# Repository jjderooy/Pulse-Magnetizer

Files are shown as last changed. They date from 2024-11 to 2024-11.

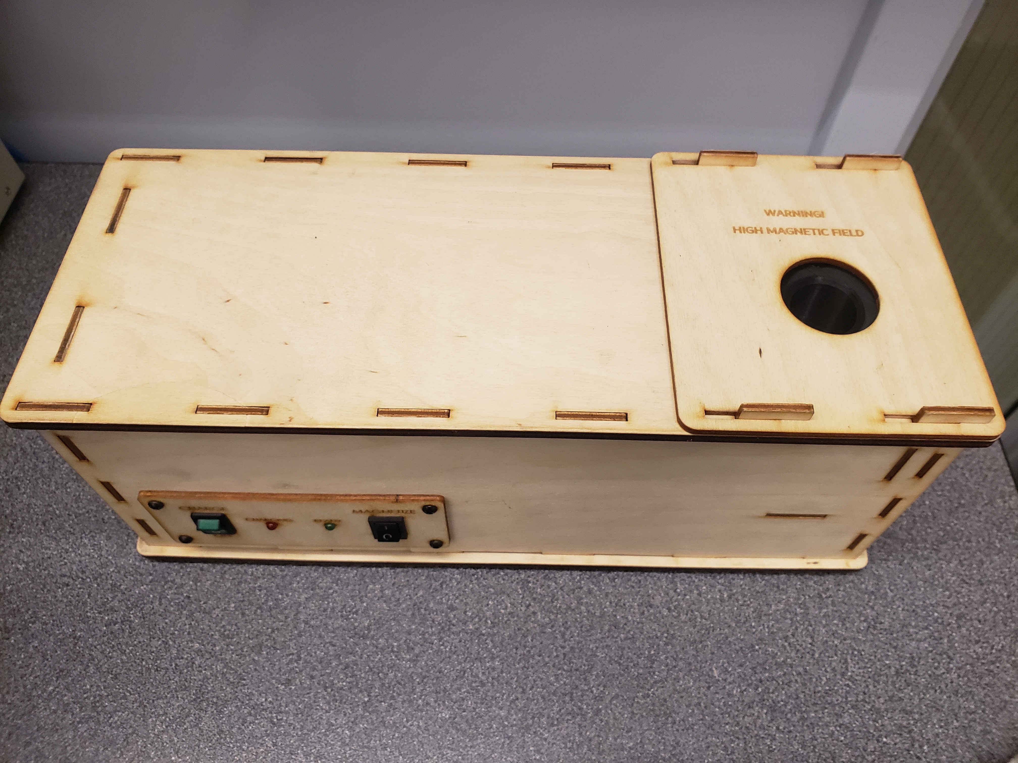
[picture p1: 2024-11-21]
Media/assembled.jpg

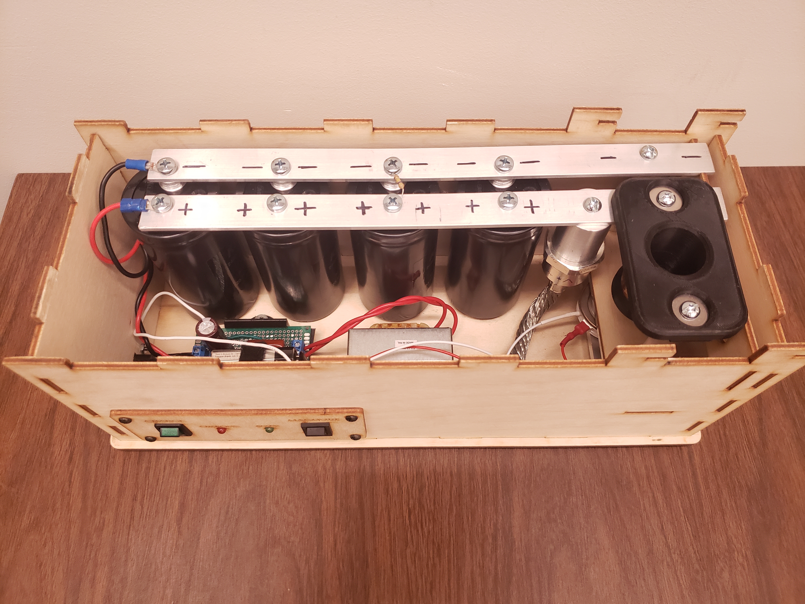
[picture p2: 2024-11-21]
Media/open_top.jpg

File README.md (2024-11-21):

# Pulse-Magnetizer
For research involving magnets, it is often required to magnetize unmagnetized permanent magnets by exposing them to a strong field. For neodymium (NdFeB) magnets, this can pose quite a challenge because the fields required to permanently magnetize them are very strong. Commercial magnetizers exist but are large and expensive and not well suited for occasional lab use.

Fortunately, Yuri Skvortsov published his design of a [pulse magnetizer](https://medium.com/@yuriy.skvortsov/pulse-re-magnetizer-for-neodymium-magnets-e5c42aefbf78) using a capacitor bank and coil to remagnetize hard drive magnets which was an excellent starting point for this project. This repository contains a modifed version of Yuri's that aims to improve safety and functionality with a basic control panel, laser cut wooden case, and basic build instructions.

## Contents
- Complete KiCAD schematic for use with 120VAC mains
- CSV bill of materials for all electrical components
- SVG for laser cut 3mm and 6mm plywood to construct housing
- STEP file CAD assembly

## Performance
A simple test to verify the functionality of the pulse magnetizer was conducted by measuring and recording the pull force of a 0.75" diameter, 0.1875" thick NdFeB disc magnet acting on a steel disk placed on a gram scale. The magnet was then heated using a heat gun to above its curie point to remove any magnetic properties. After cooling, the magnet was exposed to a full pulse from the magnetizer and measured using the gram scale again. The scale indicated the field was 98.5% of the original strength. This is not a perfect test because the grade of the magnet was not known (likely a lower grade e.g. N40), and could struggle to remagnetize higher grades like N55. Based on SPICE simulations and theoretical calculations for a 30mm diameter, 30mm long, 30 turn coil using 1mm diameter copper wire, the field strength generated was 3.5T. This could be further improved using the same dimension coil but with 1.5mm diameter wire (by reducing inductance and resistance allowing more current flow), to generate a 4.3T field. This is plenty strong for even N55 magnets.

## Safety
This device deals with lethally high voltages, and capacitors that can maintain these voltages even after the device is unplugged. Any use of this project is at your own risk.

## Build
In addition to the electronics BOM, some basic wiring hardware is needed (wire, spade connectors, soldering iron, screw terminals, proto-board). Screws are not included on the BOM, but are M5 for the capacitors, and #10 machine screws elsewhere. A small quantity of plywood (both 3mm and 6mm thickness) is needed for the lasercut enclosure. All lasercut parts are compensated for a 0.008" kerf. The user will need to create shop drawings for the machined components because this is specific to the machining capabilites at hand.

Reference the .STEP file using a CAD program (e.g. FreeCAD) for assembly of all mechanical components. Two proto-boards are needed, one for the high voltage power supply, and one for the control panel. Images are included for a rough layout, but overall are left to the user to implement.

The spool for the coil is designed for 3D printing to allow customization of the coil dimensions. Care must be taken when manufacturing coils due to the high forces exerted on conductors during magnetizing. The coil had a tendancy to squish axially causing turns of the coil to overlap reducing uniformity of the field. To prevent this, it is recommended to wind the coil tightly and coat lightly with adhesive such as cyanoacrylate before wrapping with a few layers of polyimide (kapton) tape.

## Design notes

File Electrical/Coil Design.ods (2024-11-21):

Use this sheet to optimize coils. More turns increases the field strength, but also increases resistance and inductance which limit current and reduce field strength. Use the computed resistance and inductance values in a KiCAD or LTspice simulator with a 9600uF 340V capacitor bank to determine current. Use this peak current to calculate the B field. Nd magnets require at least 2T to be magnetized, but note that this calculator assumes an ideal solenoid which really only applies to long coils of wire so give some headroom.
Input | Intermediate | Output
Solenoid
 |  |  | 30L 30ID 1mm wire
Parameter | Value | Units | Field: 3.5T
Length | 30.00 | mm
Inner Dia. | 30.00 | mm
Outer Dia. | 32.00 | mm
Copper Dia. | 1.00 | mm
Conductivity | 5.80E+07 | S/m
Rel. Perm | 1.00 | -
Vac. Perm | 1.26E-06 | -
Wire Dia. | 1.01 | mm | 30L 30ID 1.5mm wire
Turns/Length | 30.00 | - | Field: 4.3T
Layers | 0.99 | -
Total Turns | 30.00 | -
Total Length | 2.86 | m
Resistance | 0.063 | Ohm
Inductance | 28.45 | uH
Current | 3,000.00 | A
B | 3.770 | T

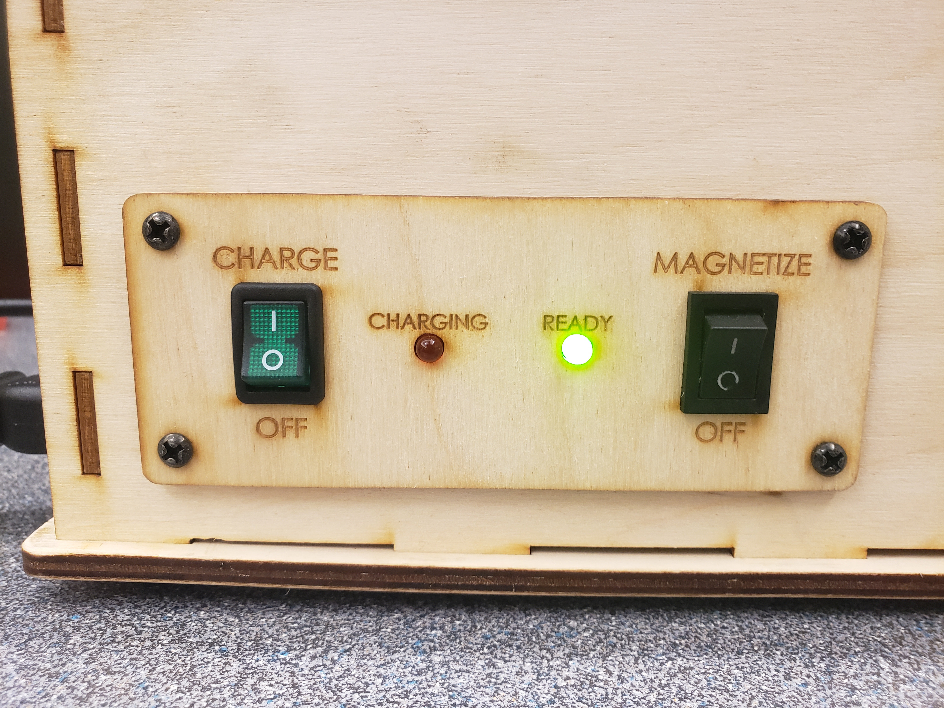
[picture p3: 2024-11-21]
Media/control_panel.jpg

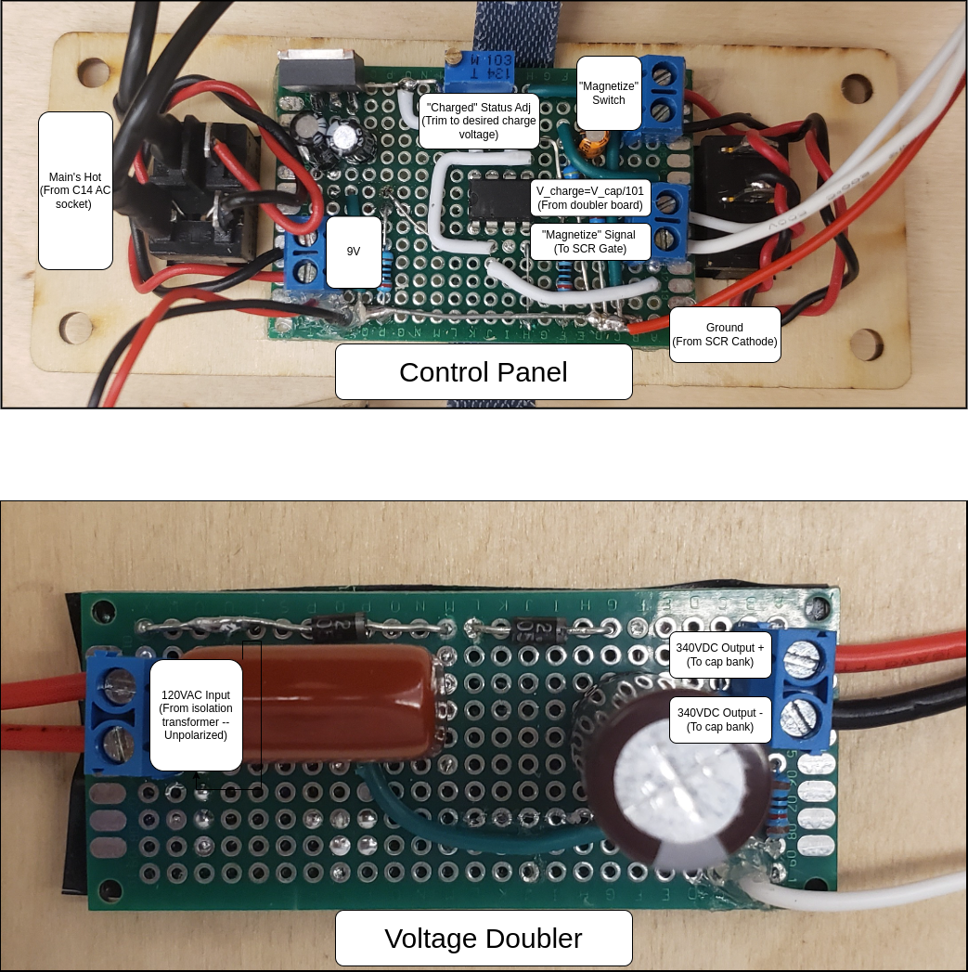
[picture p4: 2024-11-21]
Media/proto_boards.png

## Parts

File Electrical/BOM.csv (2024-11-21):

Index | Manufacturer Part Number | Manufacturer Name | Description | Requested Quantity 1 | Pack Quantity 1 | Pack Type 1 | Digi-Key Part Number 1 | Unit Price 1 | Extended Price 1 | Minimum Order Quantity 1
1 | N-48X | Triad Magnetics | XFRMR ISOL 115V TO 115V 15VA | 1 | 1 | Box | 237-1856-ND | 22.25 | $22.25 | 1
2 | ALS80A242KF400 | KEMET | CAP ALUM 2400UF 20% 400V SCREW | 4 | 4 | Bulk | ALS80A242KF400-ND | 55.41 | $221.64 | 1
3 | 1N4005-TP | Micro Commercial Co | DIODE GEN PURP 600V 1A DO41 | 10 | 10 | Cut Tape (CT) | 1N4005-TPMSCT-ND | 0.173 | $1.73 | 1
4 | VS-400U160D | Vishay General Semiconductor - Diodes Division | DIODE GP 1.6KV 400A DO205AB | 1 | 1 | Bulk | VS-400U160DGI-ND | 85.24 | $85.24 | 1
5 | VS-ST330C12C0 | Vishay General Semiconductor - Diodes Division | SCR 1.2KV 1420A TO200AB | 1 | 1 | Bulk | ST330C12C0-ND | 138.1 | $138.10 | 1
6 | CF12JT470K | Stackpole Electronics Inc | RES 470K OHM 5% 1/2W AXIAL | 1 | 1 | Cut Tape (CT) | CF12JT470KCT-ND | 0.16 | $0.16 | 1
7 | ECW-FD2W225J | Panasonic Electronic Components | CAP FILM 2.2UF 5% 450VDC RADIAL | 2 | 2 | Bulk | PCF1609-ND | 1.09 | $2.18 | 1
8 | 703W-00/04 | Qualtek | PWR ENT RCPT IEC320-C14 PANEL QC | 1 | 1 | Bulk | Q212-ND | 1.56 | $1.56 | 1
9 | RA1113112R | E-Switch | SWITCH ROCKER SPST 10A 125V | 1 | 1 | Bulk | EG5619-ND | 1 | $1.00 | 1
10 | LRA32H2FBBNN | ZF Electronics | SWITCH ROCKER DPST 10A 125V | 1 | 1 | Bulk | CH770-ND | 2.67 | $2.67 | 1
11 | 232 | Keystone Electronics | BATT CONNECTOR SNAP 9V 4" LEADS | 1 | 1 | Bulk | 36-232-ND | 0.9 | $0.90 | 1
12 | CF14JT200R | Stackpole Electronics Inc | RES 200 OHM 5% 1/4W AXIAL | 10 | 10 | Cut Tape (CT) | CF14JT200RCT-ND | 0.055 | $0.55 | 1
13 | CF14JT1M00 | Stackpole Electronics Inc | RES 1M OHM 5% 1/4W AXIAL | 10 | 10 | Cut Tape (CT) | CF14JT1M00CT-ND | 0.055 | $0.55 | 1
14 | CF14JT10K0 | Stackpole Electronics Inc | RES 10K OHM 5% 1/4W AXIAL | 10 | 10 | Cut Tape (CT) | CF14JT10K0CT-ND | 0.055 | $0.55 | 1
15 | CF14JT4K70 | Stackpole Electronics Inc | RES 4.7K OHM 5% 1/4W AXIAL | 10 | 10 | Cut Tape (CT) | CF14JT4K70CT-ND | 0.055 | $0.55 | 1
16 | ECA-1JM100LW | Panasonic Electronic Components | CAP ALUM 10UF 20% 63V RADIAL TH | 1 | 1 | Cut Tape (CT) | P19535CT-ND | 0.22 | $0.22 | 1
17 | LM358P | Texas Instruments | IC OPAMP GP 2 CIRCUIT 8DIP | 1 | 1 | Tube | 296-1395-5-ND | 0.36 | $0.36 | 1
18 | LM7805CT/NOPB | Texas Instruments | IC REG LINEAR 5V 1A TO220-3 | 1 | 1 | Tube | 296-47192-ND | 2.72 | $2.72 | 1
19 | N6L30T0N-103-3030 | Amphenol Piher Sensing Systems | TRIMMER 10K OHM 0.1W PC PIN TOP | 1 | 1 | Bulk | 1993-N6L30T0N-103-3030-ND | 0.72 | $0.72 | 1
20 | C320C104K5R5TA | KEMET | CAP CER 0.1UF 50V X7R RADIAL | 2 | 2 | Bulk | 399-4264-ND | 0.35 | $0.70 | 1
21 | MT4118-HR-A | Marktech Optoelectronics | LED RED DIFFUSED 5MM ROUND T/H | 1 | 1 | Bulk | 1125-1188-ND | 0.47 | $0.47 | 1
22 | MT2118-G-A | Marktech Optoelectronics | LED GREEN DIFFUSED 5MM ROUND T/H | 1 | 1 | Bulk | 1125-1184-ND | 0.45 | $0.45 | 1

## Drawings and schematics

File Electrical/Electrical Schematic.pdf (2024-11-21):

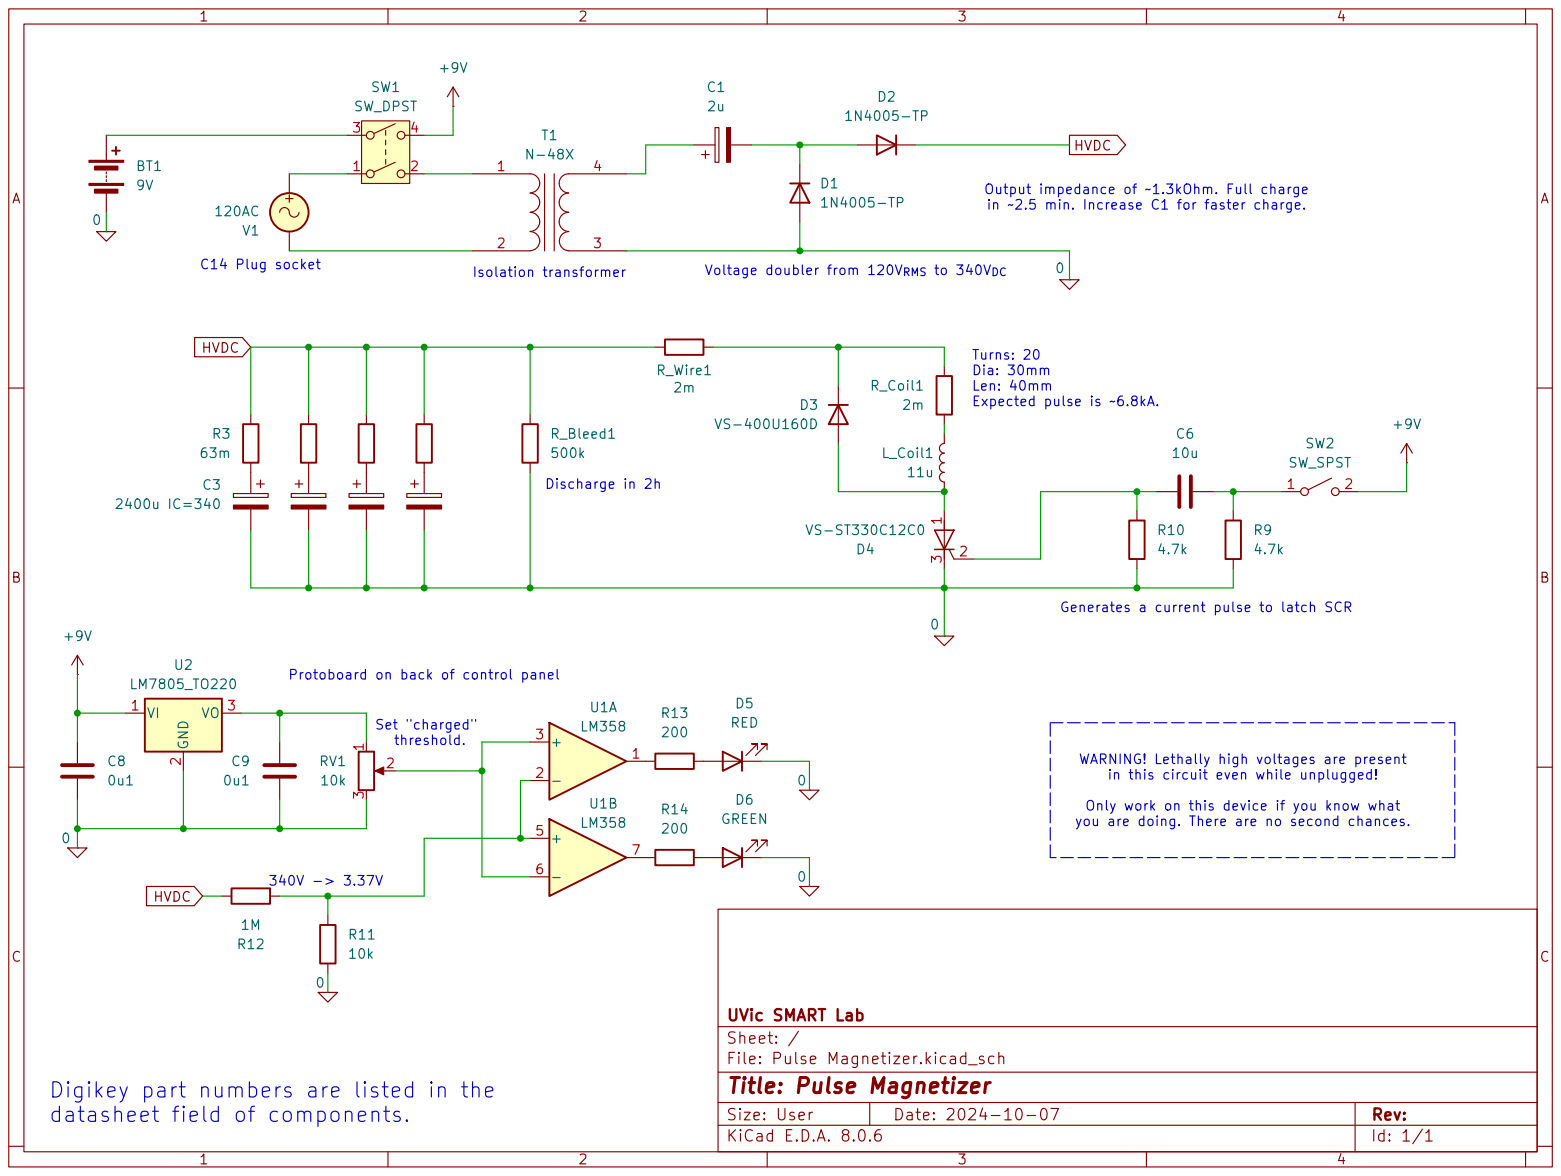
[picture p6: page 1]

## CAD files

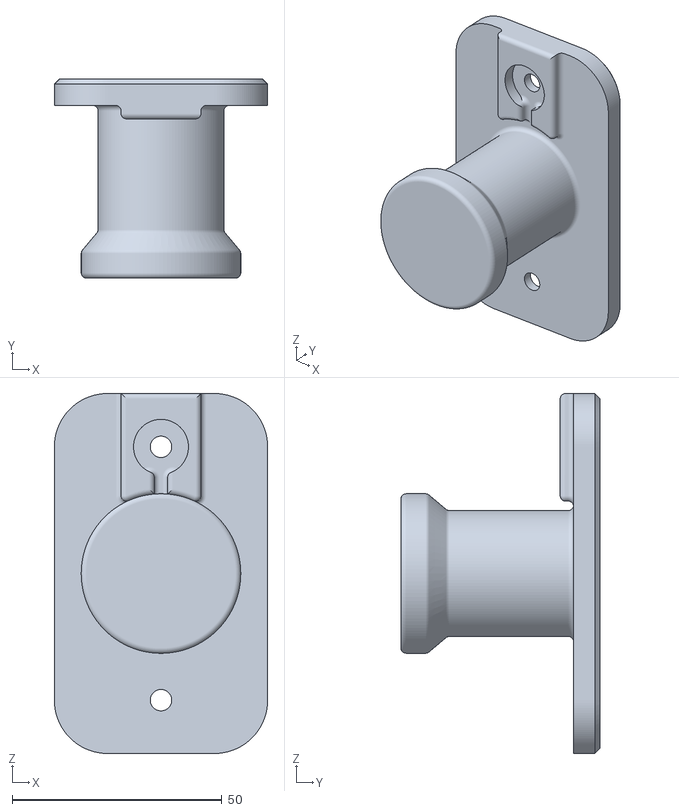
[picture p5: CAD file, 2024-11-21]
Mechanical/Coil Spool.stl
50.8 x 47.5 x 85.7
